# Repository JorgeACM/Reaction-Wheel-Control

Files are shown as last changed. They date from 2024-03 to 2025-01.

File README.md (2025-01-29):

# 🚀 Reaction Wheel Control of an Air-Bearing Floating Robot  

## 📌 Overview  
This repository contains the code and simulation models for the **attitude control system** of an **air-bearing floating robot** using a **reaction wheel with a single degree of freedom**. This project was developed as part of the **MSc in Space Engineering** at the **University of Surrey - Surrey Space Centre**, aiming to simulate **near-frictionless conditions** similar to those in space.  

## 📂 Repository Structure  
```
Reaction-Wheel-Control/
│── CAD/                     # CAD files of the floating robot assembly
│── CAD_Images/              # Images of the robot model
│── Images/                  # Simulink Simulations ScreenShots
│── src/                     # Simulink models and MATLAB scripts for calculations and system simulations  
│── Documents/               # Project-related documents and reports  
│── README.md                # This file  
```

## ⚙️ Setup & Usage  

### 1️⃣ Initialize System Variables  
Before running any **Simulink model**, execute the following MATLAB script to load all system variables into the workspace:  
```matlab
run('src/SystemVariables.m');
```
### 2️⃣ Running Simulink Models  
To simulate the **attitude dynamics and control using a reaction wheel**, follow these steps:  

1. Open **MATLAB**.  
2. Navigate to the `src/` directory.  
3. Open the required Simulink model: `src/CompleteControl_SimpleDC.slx`
4. Click **Run** to start the simulation.  

### 3️⃣ Viewing the Full CAD Assembly  
To visualize the **complete robot assembly**, follow these steps:  

1. Open **SolidWorks**.  
2. Navigate to the `CAD/` directory.  
3. Open the following file:  
`CAD/Floating Robot 2.SLDASM`
4. The full 3D model of the robot should load in SolidWorks.

## 🛠 System Components  
- **Reaction Wheel**: Provides the necessary torque for attitude control.  
- **BLDC Motor**: Controls the reaction wheel’s angular velocity.  
- **Air-Bearing System**: Reduces friction, simulating space-like conditions.  
- **MATLAB/Simulink**: Used for system modeling, simulation, and control design.  

## 📌 Research Contributions  
This project contributes to the **development of reaction wheel-based attitude control systems**, which are widely used in **CubeSats** and other small spacecraft. The system has been validated through numerical simulations and CAD modeling, providing a foundation for further experimental testing.  

## 📖 References  
For a detailed explanation of the system design, refer to the **thesis document** included in the `Documents/` folder:
`Documents/Reaction_Wheel_Control_of_an_Air-Bearing_Floating_Robot.pdf`

## 📝 License  
© 2024 Jorge Antonio Chavarín Montoya.  
This project is part of academic research and is distributed for educational and research purposes.

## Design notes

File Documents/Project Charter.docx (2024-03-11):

GENERAL PROJECT INFORMATION
Project Name | Project ID / Number
Reaction Wheel Control of Air-Bearing Floating Robots
| Date Prepared
| 08-March-2023

Project Sponsor

University of Surrey
Project Manager | Customer
Jorge Chavarin | -

Other Project Stakeholders

Surrey Space Centre

Dr. Nicola Baresi

Stakeholders Responsibilities

Jorge Chavarin – Master student build the project,

Dr. Nicola Baresi – Project Tutor,

University of Surrey / Surrey Space Centre – Lend facilities and tools to do the project.

SCOPE STATEMENT

Business Need and Problem Statement

The Air-Bearing floating robot of the Surrey Space Centre, needs an Attitude Control System to be able to orientate to a specific point (angle) detected by a camera in the “sky”.

Project Goals and Objectives (Deliverables)

- Design a 3D model of the robot, within any assemble errors, and find its moment of inertia, using SolidWorks, within the first 2 weeks.
  - FEPS Faculty Admin, Luca Ferrian, to provide partial design of the robot, missing parts should be created in 3D with same measurements as the real ones from the floating robot.
  - 1-2 weeks
- Design and model the Reaction Wheel system in SolidWorks, according to robot measures. The system includes the motor, wheel, bearings, shaft, sensors (gyroscopes), frame and adaptors, electronics (Raspberry Pi, camera) and any other part used for the Attitude Control system. (1-2 weeks)
- Design a control law for the system in Simulink in order to have a correct reaction of the simulated plant (Software in the Loop).
- Robot will rotate precisely to the given angle in a time frame.

Benefits

Metrics

- Angle precision.
- Time of rotation / angular velocity of the robot.

SUPPORTING DETAIL

Cost

- MATLAB with Simulink license (TBD)
- SolidWorks license (TBD)
- Manufacturing /3D print of pieces (TBD)
- Hardware (£105 - £150)
  - Raspberry Pi (£64-£78)
  - Raspberry case with Fan (£10)
  - Camera (£26-£57)
  - Camera Mount (£5)
  - BDCL motor 536-6024 (£54.84)

Project Completion Date

- First Report: 13/03/2023
- Interim Review: 29/04/2023
- Final Report: 03/09/2023
- Viva Presentation: 03/09/2024 – 15/09/2023

Assumptions

Links to Strategic Objectives and/or Other Projects

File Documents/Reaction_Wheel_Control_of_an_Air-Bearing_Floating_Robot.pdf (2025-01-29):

Jorge Antonio Chavarín Montoya, MSc dissertation

- i -

# Reaction Wheel Control of an Air-Bearing Floating

# Robot

## Jorge Antonio Chavarín Montoya

## Master of Science in Space Engineering

## from the

## University of Surrey

## School of Computer Science and Electronic Engineering

## Faculty of Engineering and Physical Sciences

## University of Surrey

## Guildford, Surrey, GU2 7XH, UK

## September 2024

## Supervised by: Nicola Baresi

## ©Jorge Antonio Chavarín Montoya 2024

- ii -

## DECLARATION OF ORIGINALITY

I confirm that the project dissertation I am submitting is entirely my own work and that any ma-

terial used from other sources has been clearly identified and properly acknowledged and referenced.

In submitting this final version of my report to the JISC anti-plagiarism software resource, I confirm

that my work does not contravene the university regulations on plagiarism as described in the Student

Handbook. In so doing I also acknowledge that I may be held to account for any particular instances

of uncited work detected by the JISC anti-plagiarism software, or as may be found by the project

examiner or project organiser. I also understand that if an allegation of plagiarism is upheld via an

Academic Misconduct Hearing, then I may forfeit any credit for this module, or a more severe pen-

alty may be agreed.

Reaction Wheel Control Of An Air-Bearing Floating Robot

Jorge Antonio Chavarín Montoya

Author Signature | Date: 10/09/2024

Supervisor’s name: Dr. Nicola Baresi

- iii -

## WORD COUNT

Number of Pages: 65

Number of Words: 13406

- iv -

## ABSTRACT

The main objective of this project is to design and implement an Attitude Control System (ACS)

utilizing a single-degree-of-freedom Reaction Wheel for an air-bearing floating robot owned by the

Surrey Space Centre. This system controls the robot’s simulating near-frictionless conditions like to

those in space. The ACS uses mathematical models, control laws, and software-in-the-loop (SIL)

testing to guarantee that the system meets operational standards.

The reaction wheel system, powered by a brushless DC (BLDC) motor, generates the torque re-

quired to adjust the robot’s attitude. The BLDC motor allows precise control over the wheel’s speed,

which directly influences the accurate control of the robot’s orientation. The CAD design and mate-

rial selection were important steps for the smooth integration of all components, helping the system

function as a whole.

The control law achieved in this project lets the system perform attitude adjustments and orienta-

tion changes with accuracy. Initial tests of the reaction wheel showed positive results, giving a solid

base for implementing a functional prototype of the ACS as the next step.

This research contributes to the growing knowledge of attitude control systems for small satellites,

such as CubeSats. The results are a control system that can be tested in real-time simulations, and a

CAD model of the robot useful for future components integrations. This work has potential use in

academic and industrial settings, especially in satellite development.

- v -

## TABLE OF CONTENTS

Declaration of originality | ii
Word Count | iii
Abstract | iv
Table of Contents | v
List of Figures | vii
1 Introduction | 2
1.1 Background and Context | 2
1.2 Scope and Objectives | 3
1.3 Achievements | 3
1.4 Overview of Dissertation | 4
2 Background Theory and Literature Review | 5
2.1 Air-bearing Floating Robots | 5
2.2 Attitude Dynamics | 6
2.3 Reaction Wheels | 8
2.4 Linear Control Theory | 10
2.4.1 Controllability | 10
2.4.2 Observability | 10
2.4.3 Full-state feedback controller | 10
2.5 MATLAB / Simulink | 11
2.6 Summary | 12
3 Robot Model | 13
3.1 Introduction | 13
3.2 Air-Bearing Floating Robot | 13
3.2.1 CAD Design | 13
3.2.2 Inertia measurements | 15
3.3 Reaction Wheel Design | 16
3.3.1 BLDC Motors vs DC Motors | 16
3.3.2 Wheel measurement & material selection | 18
3.3.3 CAD Design | 19
3.3.4 Inertia | 21
3.4 Summary | 22
4 Robot Attitude dynamics and Control via Reaction Wheel | 23
4.1 Introduction | 23
4.2 Coordinate Frames | 23
4.2.1 Inertial Frame vs Rotational Frame | 23

- vi -
4.2.2 Table Frame | 24
4.2.3 Body Frame | 24
4.2.4 Orbit Frame | 24
4.3 Robot Kinematics Equations – Passive Control of Reaction Wheel | 24
4.3.1 Controllability of Outer Loop | 25
4.3.2 Observability of Outer Loop | 26
4.4 Control Torque with Reaction Wheels in Passive Mode | 26
4.5 Reaction Wheel dynamics | 26
4.5.1 Motor Electrical & Mechanical Equations | 26
4.5.2 Three-Constant motor model DC representation | 27
4.6 Summary of Mathematical Developments | 30
5 Numerical Simulations in Simulink | 30
5.1 Introduction | 30
5.2 Simulink Models | 31
5.2.1 Outer Loop | 31
5.2.2 Inner Loop | 34
5.3 Numerical Experiments | 37
5.4 Summary | 40
6 Conclusion | 41
6.1 Evaluation | 42
6.2 Future Work | 43
6.2.1 PWM Implementation for BLDC Motors | 43
6.2.2 No Body and Axis of Inertia Alignment | 43
7 References | 44
8 Appendix | 46
8.1 APPENDIX A: Coordinate System Definition (CSD) Document | 46
1. Overview of Coordinate Systems | 46
1.1 Summary | 46
1.2 Frank Diagram | 46
2. Coordinate Systems | 47
2.1 | Attitude Reference Frames | 47
2.2 | Mechanical Frames | 49
APPENDIX B: MATLAB Scripts & Simulink Models | 58

- vii -

## LIST OF FIGURES

Figure 2-1 – ESA Air-Bearing Floating Robot. Credit: ESA-G/Porter – CC BY-SA 3.0 IGO [4]..... 5

Figure 2-2 - Full-State Feedback Controller Block Diagram | 11
Figure 3-1 - Air-bearing Floating Robot from Surrey Space Centre | 13
Figure 3-2 - CAD Design with subsystems in distinct levels | 14
Figure 3-3 - Top-view of Robot showing counterweights circled in yellow | 15

Figure 3-4 - Traditional DC brushed motor with a permanent magnet stator. Credit: ZGC Motor [13].

| 16
Figure 3-5 - Brushed Motor vs Brushless DC (BLDC) Motor [14] | 17
Figure 3-6 - GM3506 BLDC Motor with AS5048A Encoder integrated [17] | 17
Figure 3-7 – 2-D Drawing of Reaction Wheel. Measurements in mm | 19
Figure 3-8 - Wheel CAD | 19
Figure 3-9 - Reaction Wheel System Assembly | 20
Figure 3-10 - Motor Base with measurements | 20
Figure 4-1 – Three-constant motor model DC representation of a three-phase motor | 27
Figure 4-2 - Momentum exchange devise model | 28
Figure 4-3 - Reaction Wheel in torque mode | 29
Figure 5-1 - Outer Loop - Robot Attitude Control | 31
Figure 5-2 - Open-Loop Step Response of Attitude Control | 32
Figure 5-3 - Step Response for different Poles | 33
Figure 5-4 – Poles location using Full-State Feedback Control, P1(-4.89,0), P2(-3.998,0) | 33
Figure 5-5 - Closed Loop Step Response of State Feedback Controller | 34
Figure 5-6 -Simplified Torque Mode of a Reaction Wheel | 34

Figure 5-7 - Step Response of Simplified Torque Mode Reaction Wheel without limited Torque. 36

Figure 5-8 - Pole location of Reaction Wheel System | 36
Figure 5-9 - Complete Robot Attitude Controller | 37
Figure 5-10 – Step response of amplitude 10-degrees. Gains: Kp = 1.0002, Kd = 04547 | 38
Figure 5-11 - Step response for a 170-degrees step. Gains Kp = 1.0002, Kd = 04547 | 38

Figure 5-12 – Top: Comparison between the angular velocity of the robot and the reaction wheel.

Bottom: Commanded torque vs actual torque reaction of the robot | 39
Figure 5-13 – Plant Step response of amplitude 170 (deg.). Gains Kp = 0.9 & Kd = 1 | 40
Figure 6-1 - PWM Sensorless Controller of a BLDC motor | 43
Figure 8-1: Right hand Rule | 46

Figure 8-2. Frank Diagram. “T” stands for translation, “R” for rotation and “A” refers to the Attitude

Dynamics equations | 46
Figure 8-3: GTS reference frame | 47

- viii -
Figure 8-4: RTS Reference Frame | 48
Figure 8-5. Body Fixed Reference Frame & Mechanical CAD Frame Below | 50
Figure 8-6. CAD Reference Frame. The point is at O (0,0,0) of the CAD Frame | 52
Figure 8-7. Reaction Wheel Frame vs Mechanical CAD Frame | 53
Figure 8-8. Camera Reference Frame (CAM), Mechanical Frame (CAD) | 56
Figure 8-9. Distance from Mechanical Frame to Gyro Frame | 57
Figure 8-10. Gyroscope Frame and Mechanical CAD Frame | 57

- 2 -

## 1 INTRODUCTION

Attitude control systems (ACS) are important for spacecraft and robotic platforms that need to func-

tion in frictionless environments. These systems help a satellite or robot reach and maintain the

desired orientation, which is crucial for mission success. In this project, an ACS was designed and

implemented for a floating robot that uses a reaction wheel as its main actuator.

The system's goal is to control the robot's orientation with high precision in real-time. This is

accomplished by combining hardware components such as sensors and actuators with control algo-

rithms tested through software-in-the-loop simulations, being the latter the main objective of this

project. The floating platform, built to simulate microgravity conditions, provides a way to test the

ACS’s performance in real conditions.

### 1.1 Background and Context

In recent years, reaction wheel systems have become one of the most used attitude control systems

for small satellites due to their accuracy capacity and no fuel necessity. Meanwhile, the need to test

these and other spacecraft subsystems on the ground caused scientists to develop different ways to

simulate space environments. Air-bearing spacecraft simulators have been used to test attitude deter-

mination and control systems for more than 45 years [1]. These robots use air-bearing technologies

to float over surfaces, therefore simulating minimal torque environments.

Reaction Wheels are used to precisely orientate a small spacecraft in a desired direction, so they

are tested in air-bearing floating robots. By using the principle of conservation of angular momentum,

reaction wheels provide the required torque to adjust the robot's orientation in response to external

disturbances or desired manoeuvres. The system comprises one or more motor-driven wheels

mounted on the satellite's body that accumulate rotational energy. Any change in the angular accel-

eration of the wheel causes an equal and opposite reaction, thereby enabling the robot to achieve a

specific angular momentum.

Space applications avoid mechanical contact, such as bearings, gears, or motor brushes. Conse-

quently, brushless DC motors (BLDC) are becoming more relevant, as they have longer lifespan,

higher torque and efficiency, and low heat dissipation than traditional DC motors [2].

The objective of this project is to design, manufacture, and test a single-degree-of-freedom reac-

tion wheel system for a floating robot. With the aid of existing literature and practical observations,

this research seeks to explain the fundamental principles, design considerations, and implementation

challenges associated with the integration of a reaction wheel control system into ait-bearing floating

robots.

- 3 -

### 1.2 Scope (http://www.cs.stir.ac.uk/~kjt/research/conformed.html) and Objectives

1. CAD design of air-bearing device equipped with a Reaction Wheel assembly, the model shall

include a power source, a raspberry pi, and IMU unit, and a camera module to estimate the

attitude of the “spacecraft”, the reaction wheel and motor shall be sized and included in the

model to enable attitude control experiments.

2. Develop a PID controller in MATLAB Simulink for the 1-DOF attitude control of an air-

bearing robot on granite table by means of a reaction wheel.

3. The robotshall re-orient itself based on commanded “desired” attitude configurations, in Sim-

ulink simulations.

To achieve the first objective, a detailed CAD model of the air-bearing floating robot equipped

with a reaction wheel assembly was created using SolidWorks. The design included a power source

(LiPo Battery), a Raspberry Pi, a Gyroscope, and a camera module for estimate the robot’s attitude.

The reaction wheel and motor were sized and integrated into the model according to the robots wight

and inertia measurements.

For the second objective, a controller was developed in MATLAB and Simulink to handle the 1-

DOF attitude control of the robot using the reaction wheel. Main controller gains were deduced math-

ematically, and subsequent real-time simulations were performed to adjust the controller.

Finally, simulations were run to check that the robot could reorient itself based on user-com-

manded “desired” attitude configurations. The Simulink tests showed that the robot adjusted its

orientation smooth and correctly, according to the input commands. While physical tests have yet to

be completed, the simulations suggest that the system meets the expectations for this task..

### 1.3 Achievements

The main accomplishment of this project is the successful development of an Attitude Control Sys-

tem (ACS), which includes both mechanical design of its components and the CAD design of the

floating robot SolidWorks. The 3D model created ensures the compatibility among its components

and gives a framework for integrating future projects, making it easier to adapt or extend the system

as needed. This model supports future work by offering a solid base for additional modifications.

Additionally, the mathematical model for the robot and the Acs, was used to simulate the dynam-

ics of both plants. This model makes possible to predict the system’s behaviour, forming the basis

for the control law proposed in this project. It also offers valuable insight for potential improvements

or alternative control strategies that could be explored in future research.

The project also achieved successful software-in-the-Loop (SIL) testing using Simulink and

MATLAB. This testing confirmed that the developed control law functions effectively and helped in

- 4 -

fine-tuning it by running real-time simulations of the system’s performance. Overall, these achieve-

ments lay a strong foundation for future development in attitude control systems for small platforms.

### 1.4 Overview of Dissertation

This dissertation is structured into several chapters and subchapters that describe the complete pro-

cess from background review and conceptualization to implementation and testing of the system.

The first chapter provides the background and objectives of the project. It introduces the concept

of Attitude Control Systems and explains why reaction wheels are a preferred solution for small

platforms like CubeSats.

Chapter 2 gives an overview of the theoretical concepts and research that form the basis of the

Attitude Control System. It also introduces the concept of floating robots as testing mechanisms for

spacecrafts systems. Additionally, it covers attitude dynamics, reaction wheel operation and control

laws used later in the project. The chapter reviews relevant literature on the use of reaction wheels

in small satellites, which influenced the design choices made for the project.

The third chapter explains the physical and mathematical modelling of the floating robot. It in-

cludes a description of the robot’s structural components, with CAD designs created in SolidWorks.

This chapter also explains the decisions regarding material selection and measurements. It compares

conventional DC motors with Brushless DC (BLDC) motors and discusses the advantages and chal-

lenges of using BLDC motors in space applications.

Subsequently, Chapter 4 dives into the attitude dynamics of the robot and the control strategies

used to adjust its orientation. It describes the coordinate frames necessary to describe the robot’s and

components movements. Also, it focuses on the interaction between the reaction wheel and the robot,

detailing how the wheel generates the torque required to rotate the robot. The mathematical models

presented in this chapter serve as the basis for understanding the control laws developed later in the

chapter.

Chapter 5 covers the simulation work performed to test the ACS, using Simulink. The control

algorithms and models developed in the previous chapter are tested and evaluated in this section.

This chapter also details the refinement of control strategies done through real-time testing.

Finally chapter 6 gives some conclusions about the complete report, evaluates if the main objec-

tives were accomplished and give options for future work regarding reaction wheels.

- 5 -

## 2 BACKGROUND THEORY AND LITERATURE REVIEW

### 2.1 Air-bearing Floating Robots

Air-bearing floating robots have been used since the middle of last century to simulate microgravity

conditions and spacecraft dynamics on Earth, becoming essential for developing and testing real

space applications under controlled environments, such as attitude control systems or spacecraft ma-

noeuvres.

This type of robot possesses air-bearings that create a thin layer of pressurized air between the

spherical or planar surface of the robot and the surface on which it hovers, as shown in Figure 2-1.

The pressurized air is expelled through small holes on the base of the robot, forming an air layer that

drastically reduces the friction between the robot and the surface [3]. As a result, the robot can move

freely in any direction with lower resistance, simulating the space microgravity environment.

The air system allows the robots to simulate an almost frictionless environment. By adjusting the

pressure and direction of the air expelled, the movements of the robots can be controlled with preci-

sion, which allows them to replicate real dynamics conditions that objects would experiment with in

space, such as the absence of gravity and atmospheric drag.

Figure 2-1 – ESA Air-Bearing Floating Robot. Credit: ESA-G/Porter – CC BY-SA 3.0 IGO [4].

Air-bearing platforms have evolved significantly over time. While early systems were initially

designed for academic purposes, they quickly became indispensable for testing real spacecraft appli-

cations. Floating robots allows the simulation of rotational dynamics in an almost frictionless

environment [1].

- 6 -

In recent years, the capabilities of air-bearing floating robots have improved thanks to technolog-

ical advancements, enabling them to emulate more complex manoeuvres, such as multiple axes

satellite rotations, without the friction restriction of Earth surfaces. Additionally, the continuous evo-

lution of air-bearing floating robots reflects the growing interest in space exploration and their

importance as space missions get more ambitious and challenging.

Floating robots have helped to develop new control law techniques, such as the ones used on

reaction wheels, implemented mainly in CubeSats to maintain their stability and orientation. How-

ever, one of the main constraints is the scale of these spacecraft’s simulators, typically limited to

small or medium-size platforms, where emulating the dynamics of bigger spacecrafts still represents

a challenge.

### 2.2 Attitude Dynamics

Attitude Dynamics refers to the study and control of orientation of a rigid body, relative to an inertial

frame of reference or another object (such as the Earth or the Sun). This field is important for the

stability and control of spacecrafts in space, as it determines how a spacecraft or satellite orientates

its principal axes with respect to such reference frame. In order to realize specific tasks like antenna

or camera pointing, or orbital manoeuvres, spacecrafts must be able to control their attitude.

The attitude of a satellite or spacecraft cand be defined through three main angles: roll, pitch and

yaw, called Eule angles(ϕ, θ, ψ). Those angles describe the rotation of the spacecraft over its principal

axes. Alternatively, rotation matrices or by an axis-angle vector (Euler axis and principal angle), that

also describe the attitude of the spacecraft. Additionally, quaternions have some advantages in terms

of describing rotations in a three-dimensional space avoiding singularities that Direction Cosine Ma-

trices (DCM) have. The selection of the appropriate representation of the attitude is related to the

requirements of the mission. While quaternions avoid mathematical singularities, Euler angles rep-

resentation is the simplest method to describe a spacecraft attitude.

Furthermore, the equations of movement for attitude dynamics of a satellite can be described of

how its orientation changes over time under the influence of external or internal torques. By control-

ling those torquesthe satellite could maintain or rotate to desired orientation. The equations of motion

for the attitude dynamics derive from the Euler equations, that describe the rotational behaviour of a

rigid body. Equation (2.1) relate the external torques acting in the spacecraft with the rate of change

of its angular momentum:

τ = ḣ

I = ḣ
B − ω × h | (2.1)

Where:

- h is the angular momentum vector,

- 7 -
- τ is the torque vector and,
- ω is the angular velocity vector.

The subscript ‘I’ on the equation above indicates a derivative in the inertial reference frame, and

the subscript ‘B’ indicates derivative in the body frame.

Moreover, the angular momentum is a vector quantity that reflects the rotational motion of a body.

Mathematically it can be defined as:

h = Iω̇ | (2.2)

Where the inertia tensor of the body, I, is matrix that represents how the mass of the satellite is

distributed in relation to their axis of rotation. If the coordinate system of the body is aligned to its

main axis, called principal axis of inertia, the matrix is diagonal, simplifying calculations associated

with the rotation of the body:
[
Ixx | 0 | 0
0 | Iyy | 0
0 | 0 | Izz] | (2.3)

Where Ixx, Iyy, and Izz are the principal moments of inertia around the x, y, and z axes, respectively.

However, it the tensor of inertia is represented in a different coordinate system (i.e. when the mas

of the body is not symmetrically distributed with respect to the principal axes), it is represented as:
[
Ixx | Ixy | Ixz
Iyx | Iyy | Iyz
Izx | Izy | Izz] | (2.4)

The products of inertia, Ixy= Iyx, Ixz= Izx, and Iyz= Izy, indicate how the rotation around one of the

axes is coupled with the rotation around another of axis.[5]

If we define the angular velocity vector as:

ω = [ωx | ωy | ωz] T
, | (2.5)

and assuming XB, YB, ZB are the principal axes of inertia, by substituting equation (2.2) in equation

(2.1) and performing the cross product, the scalar quantity of the torque for each axis can be defined

as:

τx = Ixω̇x + ωyωz(Iz − Iy) τy = Iyω̇y + ωxωz(Ix − Iz) τz = Izω̇z + ωxωy(Iy − Ix)

(2.6)

In this project, the attitude control of the floating robot is done through a reaction wheel system,

as the objective is to reorientate the robot into a desired direction.

- 8 -

### 2.3 Reaction Wheels

The principle of conservation of angular momentum establishes that in the absence of external tor-

ques, the angular momentum of a system remains constant. Reaction and momentum wheels take

advantage of this principle to control and stabilize the orientation of the spacecraft. Both systems

spin to generate a reaction torque that can change the orientation of the satellite without applying any

external forces.

The main difference between them lies in their mode of operation. On one hand, reaction wheels

are designed to adjust their rotational velocity to change the satellite’s orientation. They are used to

make precise manoeuvres by increasing or decreasing their angular velocity to generate an angular

momentum that reorientates the spacecraft in the desired direction.

On the other hand, momentum wheels spin at a high and constant velocity, providing stability to

the satellite. Their main function is to stabilize the attitude of the satellite against external disturb-

ances, keeping it in a fixed orientation. While reaction wheels focus on the adjustment and active

control of the attitude, momentum wheels centre on passive stabilization, resisting unwanted changes

in orientation [6].

Reaction Wheels are a key component in spacecraft attitude control, as they can adjust and main-

tain spacecraft orientation very precisely [7]. Their simplicity and effectiveness have made them

adopted in many space missions, from Earth observation satellites to deep space exploration.

The precise control of the spacecraft attitude by reaction wheels, without any external forces,

allows the satellite to realize sustained operations in space, where other traditional methods involving

thrusters would be limited by fuel consumption. Their capacity to generate a reaction torque inter-

nally improves the spacecraft’s lifetime. Also, it contributes to the stability and manoeuvrability

needed in complex operations, such as remote sensing operations and satellite alignment for com-

munications.

Initial designs were big and limited in their operational range, which required high amount of

power and were less flexible when performing manoeuvres. However, technology advances have led

to the development of more compact, efficient, and durable systems. Modern reaction wheels operate

at higher velocities, offering better control over the spacecraft’s angular momentum and enabling

more agile manoeuvres than before.

Integration of reaction wheel subsystems into spacecraft implies several considerations and engi-

neering challenges. One of the principal problems is wheel saturation. This occurs when the reaction

wheel reaches its maximum angular velocity and, therefore, cannot provide any extra torque. In order

to mitigate this issue, reaction wheel subsystems are commonly complemented with magnetorquers

or thrusters that work together with reaction wheels to desaturase them, restoring the capacity of the

- 9 -

wheel to provide torque. This combination ensures the continued capacity of attitude control [10].

Additionally, the configuration of the reaction wheels in the spacecraft depends on the specific

requirements for each mission, where redundancy or failure tolerance must be considered. The three

most common mount configurations of reaction wheels are Three-Orthogonal Wheel Configuration,

Four-Wheel Tetrahedral (or Pyramidal) Configuration, and Three-Wheel Skewed Configuration. The

first configuration is the simplest and widely used in missions where simplicity and power efficiency

are paramount. In this configuration, the three wheels are aligned to the principal axis of the satellite

(XB, YB, ZB), which allows them to control the attitude on the three axes with the minimum compo-

nents possible. However, this design has no redundancy, meaning the control over one of the axes

will be lost if a wheel fails.

Instead, the wheels are mounted at a non-orthogonal angle in the Four-Wheel Pyramidal Config-

uration, providing the satellite with complete redundancy. If one of the wheels fails, the remaining

three wheels can still control the spacecraft’s attitude. This configuration is the most used when reli-

ability is of high importance.

Finally, the Three-Wheel Skewed Configuration, although it is more complex than the orthogonal

configuration, offers an equilibrium between simplicity and limited redundancy. In this case, the

wheels are mounted at specific angles, which allows a certain control level even with one-wheel

failure without adding an extra wheel. This configuration is most suitable for missions with space

and budget restrictions but requires some redundancy.

With the rise of small satellites, such as CubeSats, the need for smaller and lighter reaction wheels

adjusted to space and power restrictions has emerged. Modern reaction micro-wheels maintain high

performance despite their compact size, letting these new small satellites reach the same attitude

control level as their bigger counterparts.

Furthermore, the design of satellites using Commercial Off-the-Shelf (COTS) components has

gained popularity over the last few years, including reaction wheel systems. The use of COTS lets

the owners reduce development costs and time by taking advantage of standard mechanics and elec-

tronic components that are easily available in the market. For the specific case of reaction wheels,

BLDC and DC motors of high precision and electronic controllers are the most common and acces-

sible options of COTS for reaction wheels. In this way, integration with external subsystems can be

easily achieved using standards already used and tested in other industries. Even though the use of

COTS implies certain limitations in durability or personalization of components, the technological

advancements and high-quality components available in the market have made these options more

viable for more space missions.

- 10 -

### 2.4 Linear Control Theory

Linear Control Theory is used to analyse dynamic systems described through linear differential equa-

tions. This theory is applied in control engineering to design systems that maintain stable behaviour

and respond adequately to external perturbations. Representing these systems through equations in

the state space gives a complete vision of their dynamics, considering inputs and outputs.

### 2.4.1 Controllability

A system is fully controllable if every state vector can be transferred from any initial state to any

other state in a finite time through an adequate control signal. Mathematically, a continuous system

described by:

ẋ = Ax + Bu | (2.7)
y(t) = Cx + Bu, | (2.8)

is fully controllable if the controllability matrix QC (see eq. 2.8) has a complete range. In other words,

if the range is equal to the number of stated n, where the matrix A is a n × n square matrix.

QC = [B AB A
2B … A
n−1B] | (2.9)

When the condition of full controllability is met, the system can be manipulated to reach any

desired state [11].

### 2.4.2 Observability

The observability of a system refers to the capacity to deduct the complete state of the system from

observing its outputs in a finite time. A system is fully observable if it is possible to determine the

system's initial state with the information of the output y(t) through time. Mathematically, a system

described by equations (2.7) and (2.8) is fully observable if its observability matrix from equation

(2.10) has a complete range.

QO = [C

T A

TC

T … (A

T
)

n−1C

T]

T
(2.10)

Observability is especially important in systems where not all the states can be measured directly,

and it is necessary to reconstruct the non-observable states from the available outputs.[11]

### 2.4.3 Full-state feedback controller

Through the full-state feedback controller, the system dynamics, like stability and response time, can

be adjusted by using all the state variables, see Figure 2-2. This method is based on the relation:

u = −Kx, | (2.11)

where K is the gain matrix of the controller. With a correct designed of this matrix, it is possible to

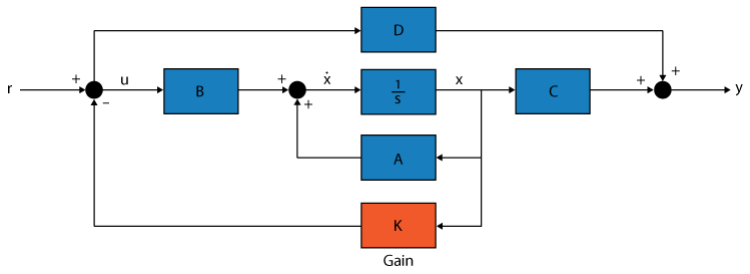
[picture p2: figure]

- 11 -

locate the poles of the system in closed loop in desired locations of the complex plane, as long as the

original system is fully controllable. This strategy is convenient when the dynamic behaviour of the

system must be adapted to design specifications.[11].

To compute the matrix K, the eigenvalues of the closed-loop system must be replaced at desired

positions to achieve the required performance. Given the state-space system from (2.7) and the con-

trol law (2.11), the closed-loop dynamics are expressed in (2.12), where r is the reference input [12].

The matrix K is selected toshift the eigenvalues of A − BK to the desired locations.

ẋ = (A − BK)x + Br | (2.12)

This type of controller requires observability from all the states, which is not always feasible in

practice. To address this, an observer is added to the system. This observer is responsible for estimat-

ing the non-measurable states from the system's outputs, thereby enhancing the controller's

effectiveness.

Figure 2-2 - Full-State Feedback Controller Block Diagram

### 2.5 MATLAB / Simulink

MATLAB is a high-level programming environment used for numerical computing, data analysis,

and algorithm development. It provides various tools for tasks such as matrix operations, plotting

functions and implementing algorithms, making it very useful for engineering and scientific appli-

cations. In this project, MATLAB was used to develop and simulate the state-space representation of

both systems, to plot almost all graphs presented in this document, and to validate the controllability

and observability of the system, among other functions that are annexed in APPENDIX B: MATLAB

Scripts & Simulink Models.

Simulink is an extension of MATLAB that provides a graphical interface for modelling, simulat-

ing and analysing dynamic systems. In this project, Simulink was used to simulate the robot’s attitude

control system, including the reaction wheel, and the controller, in block diagram. Through Simulink,

real-time simulations were performed to fine-tune the control algorithm and review the systems per-

formance.

- 12 -

### 2.6 Summary

This chapter discussed the history and significance of air-bearing floating robots in simulating mi-

crogravity and space dynamics for satellite and spacecraft applications. Attitude dynamics was

explored to describe how angular momentum can be used to rotate and change orientation of rigid

bodies. Moreover, the functionality of reaction wheel systems, in terms of how they can control and

stabilize satellites orientation by leveraging the principle of conservation of angular momentum and

the benefits of the different mount configuration of reaction wheels were also boarded. Additionally,

this chapter covered fundamental control concepts, such as controllability and observability and the

Full-State Feedback Controller, that will be used in future chapters where the complete control of the

system is going to be described.

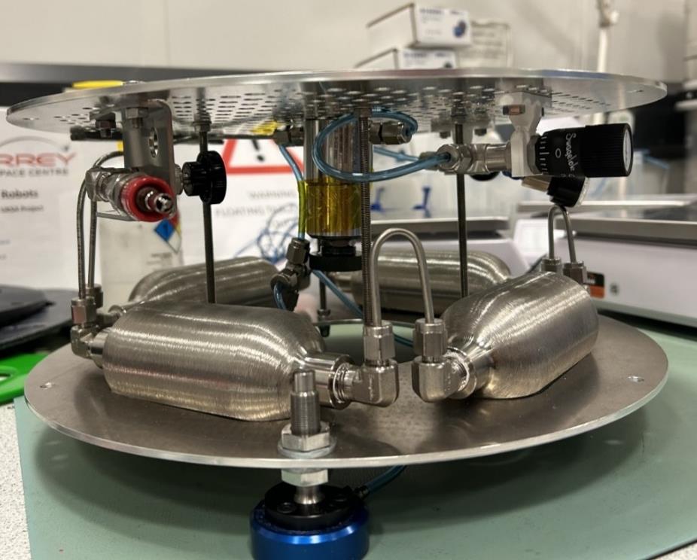
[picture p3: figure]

- 13 -

## 3 ROBOT MODEL

### 3.1 Introduction

This chapter focuses on the design and implementation of the reaction wheel system as part of the

air-bearing floating robot. A modular structure of various subsystems including a 2S-LiPo battery, a

Raspberry Pi, and an inertial measurement unit (IMU), are integrated to the main structure of the

floating robot from Surrey Space Centre. The reaction wheel, part of the Attitude Control system,

was designed using SolidWorks, ensuring it meets the required moment of inertia for accurate con-

trol. This chapter delves into the CAD design, material selection and the integration of the reaction

wheel with the motor, providing an overview of the processes involved in the design and manufacture

of an Attitude Control system.

### 3.2 Air-Bearing Floating Robot

### 3.2.1 CAD Design

The robot was modelled using SolidWorks with the objective to get the necessary measurements for

the design and integration of additional subsystems, such as the reaction wheel, and different sensors.

The robot, property of Surrey Space Centre, had three air tanks, a pressure pump, three air-bearings,

valves, and air hoses (see Figure 3-1). While most of the components’ measurements were obtained

directly from the manufacturer, some were unavailable, requiring physical measurements to be taken

manually. The upper and lower disks were made of 1060 Aluminium Alloy, while the air tanks and

valves were made of 316L Stainless-Steel to withstand high internal pressures.

Figure 3-1 - Air-bearing Floating Robot from Surrey Space Centre

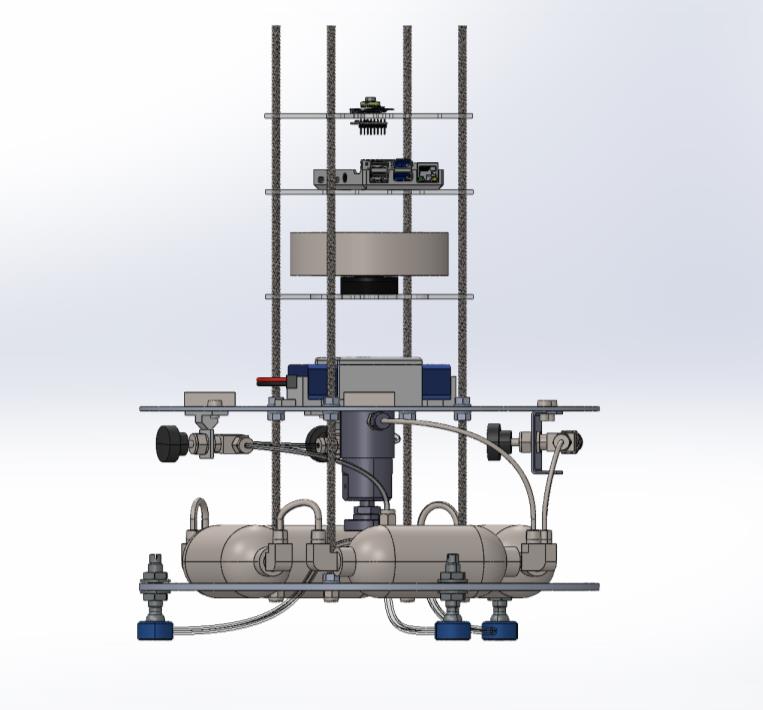
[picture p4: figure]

- 14 -

Once the main structure was modelled, electronics components were added, including a 2S-LiPo

battery, a Raspberry Pi, a Pi-Cam, and the Inertial Measurement Module (IMU) along with their

corresponding mounts. The structure of the robot was designed to be modular, with the power sub-

system, sensors, On-Board Computer, and reaction wheel placed on different levels, following the

CubeSat Standard (as shown in Figure 3-2).

The CAD model of the robot is fundamental for simulating of the entire system One of the chal-

lenges encountered was that the spacing between the holes on the top disk was not symmetrical and

the valves were also mounted asymmetrically, causing misalignments in the centre of mass and the

principal axes of inertia. A key strategy during assembly was to align the vertical axis of inertia and

the centre of mass to the geometrical centre of the robot by carefully planning the distribution of

components across the horizontal plane. The reaction wheel was positioned so that its axis of rotation

was as closely aligned as possible with the principal axis of the robot.

Figure 3-2 - CAD Design with subsystems in distinct levels.

Finally, to align the centre of mass and the vertical principal axis of inertia to the vertical axis of

the geometrical body, a pair of counterweights were added. Each counterweight was made of 316L-

SS with a mass of 100.02 g and was placed in specific locations along the horizontal plane of the

robot. Figure 3-3 shows the counterweights location on the top disk. The formula to calculate the

position to place the counterweights in each axis is:

rx =

mrobot ∙ (−∆x)

mcw

(3-1)

Where:

- rx is the location of the counterweight in one axis,

- 15 -
- mrobot is the total mass of the robot,
- ∆x is the misalignment of the centre of mass in the specific axis,
- mcw is the mass of the counterweight.

The precision and correct alignment of the centre of mass are of importance to determine the

proper behaviour of the robot particularly in the relation to the performance of the reaction wheel.

Figure 3-3 - Top-view of Robot showing counterweights circled in yellow.

### 3.2.2 Inertia measurements

From SolidWorks it was possible to obtain metrics of the robot, including weight, the Moments of

Inertia, and the position of the principal axes of inertia with respect a reference frame (explained in

the next chapter). SolidWorks name as X-axis to the minimum axis of inertia, and due to the distri-

bution of weights, that is the vertical axis. Due to the inertial vertical axis was denominated as the Z-

axis a rotation must be made. However, as the objective of the project is to rotate the robot only in

its vertical axis, so just the scalar quantity of the Moment of Inertia in its X-axis is used.

Weight: 6.1299 kg,

Moments of Inertia:

Ix = 0.0511 kg⁄m²

Iy = 0.0809 kg⁄m²

Iz = 0.0839 kg⁄m²

(3-2)

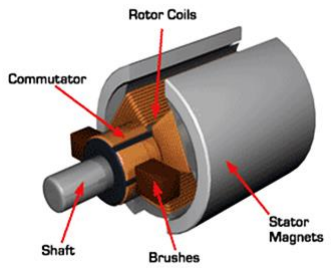
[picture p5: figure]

- 16 -

### 3.3 Reaction Wheel Design

### 3.3.1 BLDC Motors vs DC Motors

DC Motors have been used for over a century, powering from small devices to industrial machines.

However, as the demand for greater efficiency and control has grown, engineers have opted to use

brushless DC motors (BLDC). These motors have outperformed standard DC motors in many appli-

cations, particularly in space, where precision and reliability are of great interest.

Traditional DC motors operate by interacting with a static magnetic field generated by a perma-

nent magnet and a variable magnetic field produced by a coil in the rotor (see Figure 3-4). The rotor

spins when its polarity changes, which is produced by a mechanical commutator with brushes that

maintain contact with the rotating commutator [15]. This simple design allows easy speed and torque

control by adjusting the voltage supplied to the motor.

Nevertheless, the mechanical commutator represents a potential point of failure because the

brushes are subject to wear if there is no periodic maintenance, a problem in space applications where

maintenance is not feasible.

Figure 3-4 - Traditional DC brushed motor with a permanent magnet stator. Credit: ZGC Motor [13].

In contrast, BLDC Motors function with electronic commutation instead of mechanical. The rotor

has a set of permanent magnets, and the coils are fixed on the stator. The commutation of current

through the coils is managed electronically, which provides better control compared to DC motors

and removes the risk of mechanical wear (see Figure 3-5) [15] [16].

Thanks to their robustness and precision, BLDC motors are well-suited for space applications.

However, they require more complex control systemsthat includes sensors to detect the rotor position

and electronic controllers to manage commutation and convert the input voltage into a three-phase

voltage.

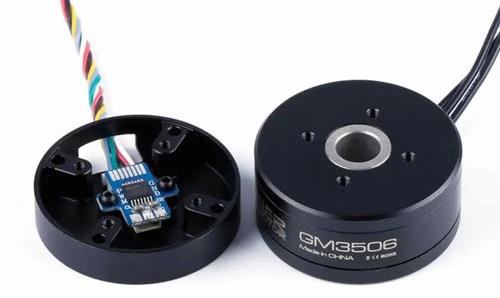
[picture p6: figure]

- 17 -

Figure 3-5 - Brushed Motor vs Brushless DC (BLDC) Motor [14].

Overall, BLDC motors offer a better efficiency -reaching up to 90%- due to the absence of energy

loss brush friction. They are also lighter and more compact than their DC counterparts for the same

power output. Brushless motors allow a more advanced control like velocity modulation or change

of spin direction without additional components but are not as straightforward to control as DC mo-

tors.

The motor used for this project is a GM3506 Brushless. A BLDC was selected as they are more

and more commonly used in space. GM3506 is powerful and reasonably priced, ensuring it can pro-

duce the necessary torque to spin the wheel. Additionally, the motor has incorporated an AS5048A

Encoder, with two types of communication, PWM or I2C, which was another reason to select it.

Table 3-1 shows the specifications of the motor.

Figure 3-6 - GM3506 BLDC Motor with AS5048A Encoder integrated [17].

- 18 -
Spec. | Value
Resistance | 5.6 Ω ± 5%
Weight | 80.3 g
No Load | Voltage | 16 V
| Current | 0.17 ± 0.05 A
| Max. Speed | 2149 – 2375 RPM
Load | Voltage | 12 V
| Current | 1 A
| Torque | 600 – 1000 g*cm

Table 3-1 - Motor GM-3506 Specifications.

The 2S-LiPo battery provides power to the motor, ensuring the motor can provide its maximum

torque indicated in the datasheet.

The maximum torque of the motor, according to Table 3-1, is τ = 600 g ∗ cm = 0.059 Nm. The

acceleration of the robot is calculated from the below equation:

α =

τ

Irobot

(3-3)

Substituting the inertia of the robot in the vertical axis (Ix), calculated at eq.(3-2), the maximum

angular acceleration that the robot can have is α = 1.154 rad
s

⁄ 2.

Lastly, using equation (3-4) the minimum time taken by the robot to execute a complete rotation

(θ = 2π) is t = 3.3 seconds, this can be very fast, however a condition in the control loop can be

added to limit the torque produced by the motor.
t = √
2θ
α

(3-4)

### 3.3.2 Wheel measurement & material selection

The wheel design includes a spoke structure in a 45-degree distribution to reduce its overall weight

while concentrating most of the mass in the outer ring compared to the disk-ring structure. The min-

imization of mass in the centre of the wheel, thanks to the spokes design, contributes to a more

efficient operation of the motor due to the reduction of the load on it. The radius of the outer and

inner circles of the ring are rout = 55 mm and rin = 40 mm, respectively, and a depth of ℎ =

30 mm. The inner disk radius is rdisk = 45 mm, see Figure 2-1. Eight spokes join ring and disk.

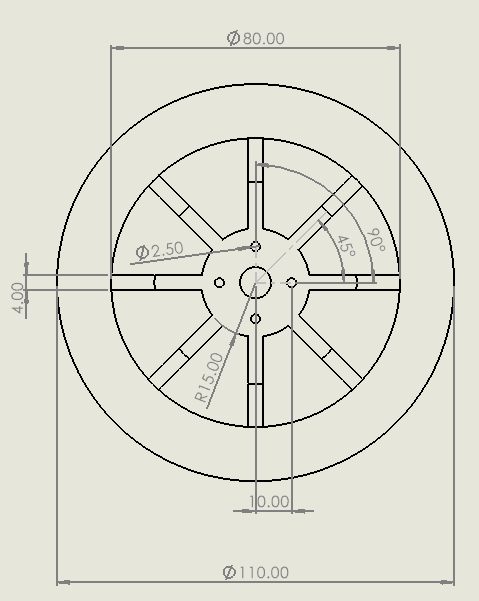
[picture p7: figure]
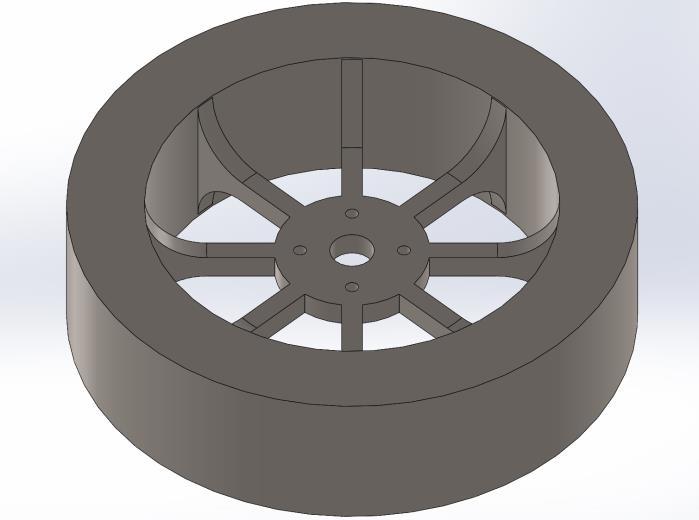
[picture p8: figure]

- 19 -

Figure 3-7 – 2-D Drawing of Reaction Wheel. Measurements in mm.

The reaction wheel was manufactured of 316L stainless steel because of its excellent resistance

to corrosion. Additionally, its high density allows smaller designs with high inertia. However, it is

also a good practice to use an aluminium alloy, depending on the mission.

The wheel design requires to take in consideration the physical and dynamic properties of the system.

### 3.3.3 CAD Design

The wheel design was also carried out using SolidWorks, with the objectives of calculating the

wheel's moment of inertia, manufacturing the wheel, and finally assembling it to the robot. The

wheel, as shown in Figure 3-8, has a central hole in the inner disk to couple it into the motor through

a shaft, and four smaller holes around (diameter = 1.25 mm) for screws to securely attach the wheel

to the motor, preventing any non-desired movement.

Figure 3-8 - Wheel CAD

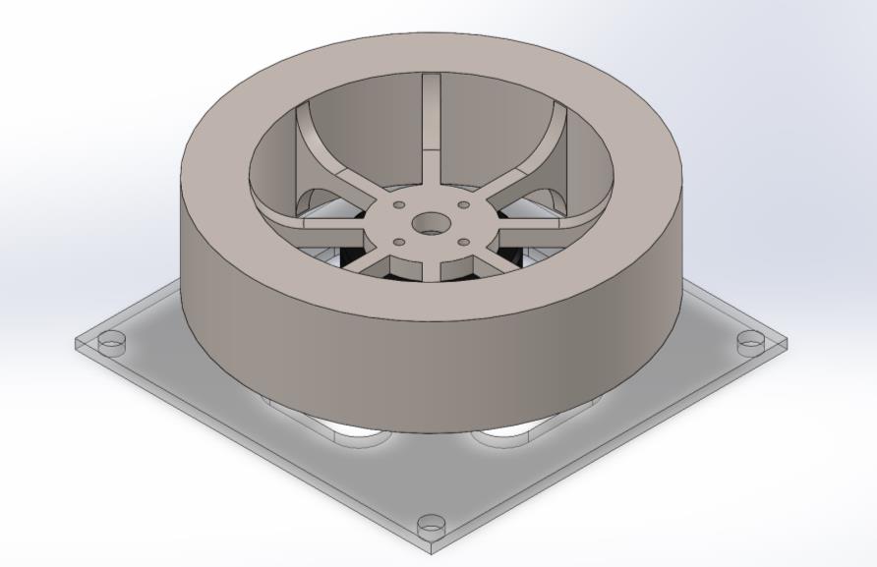
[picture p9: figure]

- 20 -

The width of the spokes and the outer ring of the wheel were adjusted to achieve the desired

moment of inertia. Figure 3-8 shows the wheel, while Figure 3-9 displays the complete reaction

wheel assembly.

Figure 3-9 - Reaction Wheel System Assembly

The base of the motor (Figure 3-10) positions the reaction wheel system at the centre of the robot,

aligning both vertical axes. The base includes four elliptical holes, with a semi-major axis of 17.5

mm and a semi-minor axis of 7.5 mm, to pass the wires from the battery to the motor and to the

raspberry in the upper level.

Figure 3-10 - Motor Base with measurements.

- 21 -

To attach the base to the main screws extending from the robot, an initial hole (diameter = 6 mm)

was designed at a 45-degree angle from the horizontal, with 70 mm from the centre of the base. The

remaining three holes were placed at the corners of a square with sides measuring 98.99 mm.

### 3.3.4 Inertia

The formula that relates the robot’s rotation time for a specific angle with the motor’s speed is given

by:

Irw ∙ ωmotor = 2 ∙ Irobot ∙

θ

trot

(3-5)

Where:

- Irw, is the inertia of the reaction wheel, including both the rotor and the wheel,
- ωmotor, is the angular velocity of the motor,
- Irobot, is the inertia of the robot about its vertical axis,
- θ, is the desired rotation angle of the robot,
- trot, is the desired time for the robot to complete the rotation.

The total inertia of the reaction wheel is the sum of the inertias of the wheel and the rotor. The

inertia of the wheel can be estimated using SolidWorks (as shown in Table 3-2), where Iz represents the inertia along the vertical axis, which aligns with the robot’s axis of rotation.

For the rotor, since the value is not in the datasheet, it can be estimated using equation (3-6) if the

mass (M) and radius (R) are known. However, these values are not specified in the datasheet. Given

that the total mass of the motor is 64 g, it is assumed that the rotor’s mass constitutes only a fraction

of this, therefore the rotor’s inertia can be neglected.

Axis | Inertia
Ix | 0.00135 kg⁄m²
Iy | 0.00135 kg⁄m²
Iz | 0.00254 kg⁄m²

Table 3-2 - Inertia Measurements of Wheel

I =

1
2
- M ∙ R

2
(3-6)

Using equation (3-5), and knowing the inertia of both the wheel and the robot, the maximum

angular velocity of the motor required to rotate the robot 360 degrees (2π radians) in 5 seconds can

- 22 -

be calculated as follows:

ωmotor = 2 ∙

Irobot

Irw

∙

θ

trot

= 2 ∙

0.0511
0.00254 ∙

2π
5

= 50.54 rad
s
⁄ | (3-7)

This angular velocity, equivalent to 483 RPM, is well within the capabilities of the motor.

The wheel was intentionally designed with a higher inertia than required to adapt to future projects

where additional components may be added to the robot.

### 3.4 Summary

The chapter provided a detailed explanation of the design and implementation of the reaction wheel

system within the air-bearing floating robot. The CAD model, developed in SolidWorks, was used

not only to calculate the moments of inertia for both the robot and the reaction wheel system, but

also to manufacture the wheel from 316L stainless steel, and any other components needed, such as

the motor base. The spoke structure design of the wheel intentionally reduce weight and maximize

the moment of inertia. Driving this wheel is the GM3506 BLDC motor, selected for its better con-

trollability and performance over traditional brushed DC motors, drives the wheel. The entire

Attitude Control System was centred to the robot’s horizontal plane and aligned with its vertical axis.

Finally, a pair of counterweights was added to shift the centre of mass to the geometrical centre of

the robot.

- 23 -

## 4 ROBOT ATTITUDE DYNAMICS AND CONTROL VIA RE-

## ACTION WHEEL

### 4.1 Introduction

Attitude determination and control is one of the main subsystems in spacecraft. This chapter exam-

ines the principles of attitude control for a floating robot, which simulates a spacecraft, using reaction

wheels. Reaction wheels allow to control precise control of orientation, without the need for external

thrusters, following the principle of conservation of angular momentum, as discussed in Section 2.3.

Moreover, the use of system coordinates is important for attitude determination. The movement

of satellites can be described in different frames, so it is important to clearly define each frame, and

the transformation matrices needed to transition between them. This chapter introduces the concepts

of inertial and rotational frames, along with the various coordinates systems used to describe the

robot’s orientation.

Additionally, the chapter covers the mathematical modelling of the robot’s dynamic behaviour,

including the equations of motion and the reaction wheel model. The control theory required to man-

age the robot’s orientation, and the approach used to verify the performance of the control system,

are also discussed in detail.

### 4.2 Coordinate Frames

This section discusses the coordinate frames used to define the motion and orientation of the air-

bearing floating robot and its subsystems. The primary frames considered are the Granite Table

Frame, the Robot’s Body Frame and the Orbit Frame. Additionally, a Mechanical Frame derived

from the CAD model is used to transfer coordinates between the body frame and the secondary

frames of the robot, including those for the reaction wheel, sensors and Raspberry Pi.

### 4.2.1 Inertial Frame vs Rotational Frame

In orbital mechanics, the absolute acceleration a⃗ of an object’s centre of mass can be measured within

a reference or inertial frame. This reference frame “has neither translational nor rotational accelera-

tion relative to fixed stars” [18] and is governed by Newton’s first law, which states that an object

will remain in its state of motion unless acted upon by an external force. Typically, the inertial refer-

ence frame is usually defined relative to fixed stars or the Earth, but for this project, it is is aligned

with the granite table.

Alternately, the rotational frame does accelerate and rotates relative to the inertial frame. In this

reference fictitious forces appear, such as centrifugal and Coriolis forces [19]. The Transport theorem

links the time derivatives of vectors in rotating and inertial frames and describes how the rotation of

- 24 -

the frame influences the observed motion of the system.

### 4.2.2 Table Frame

The Table Frame functions as the inertial reference for this project. This frame is fixed to the granite

table on which the robot moves. The X-axis aligns with the shorter side of the table, the Y-axis with

the longer side, and the Z-axis points upward, completing the coordinate triad. The origin of this

frame is set at the lower left corner of the table.

### 4.2.3 Body Frame

The body frame is a rotating reference frame attached to the robot and aligned to the robot’s centre

of mass aligned to its principal axis of inertia. This frame describes the robot’s dynamics, as the robot

moves, the axes on the horizontal plane of this frame rotate around the vertical axis, following the

robot’s orientation.

### 4.2.4 Orbit Frame

The orbit frame describes the trajectory of the robot as it moves over the table. This frame tracks the

robot’s path, with its origin is at the robot’s centre of mass. The Z-axis aligned with the table’s Z-axis

and the Y-axis aligned with the direction of the robot’s velocity.

These coordinate frames and their transformations are useful to analyse and control the robot’s

movement and orientation with respect to the granite table. For a more detailed explanation of these

primary frames as well as the secondary frames associated with the reaction wheel, sensors and CAD

reference frame please refer to “APPENDIX A: Coordinate System Definition (CSD) Document”.

### 4.3 Robot Kinematics Equations – Passive Control of Reaction Wheel

Assuming the robot has no translational motion, the angular velocity vector of the robot (body) frame

relative to the table (inertial) frame can be denoted as:

ωb⁄i = pî+ qĵ+ rk̂ | (4-1)

For this project the only rotation is about the vertical axis of the robot, a rotation matrix is Rφ

implemented to describe the rotation over the X-axis of the robot. Since the vertical axis of the robot

(X-axis), is aligned to the Z-axis of the table, an extra -90-degrees rotation matrix Rθ has to be added

to transformation from the body frame to the inertial frame, see equation (4-2).

Rφθ = [

cos θ | 0 sin θ
0 | 1 | 0
− sin θ 0 cos θ

][

1 | 0 | 0
0 cosφ −sinφ
0 sinφ | cosφ
] | (4-2)

The angular velocity ωb⁄i of the body with respect to the inertial frame is then calculated with

equation below:

- 25 -

[

p
q
r

] = [

cos θ | 0 sin θ
0 | 1 | 0
− sin θ 0 cos θ

][

1 | 0 | 0
0 cosφ −sinφ
0 sinφ cosφ

][

φ̇
0
0
] | (4-3)

Substituting θ = 90 degrees in equation (4-3) we can deduce that:
[

p
q
r

] = [

0
0
φ̇
] | (4-4)

This simplifies the equations as the model can be described only using a single angular velocity:

φ̇ = r = ω | (4-5)

From the Euler’s Moment Equations (2.6), applied to a single rotation the rate of change of the

angular momentum of the robot can be defined as:

τ = ω̇ ∙ Jb | (4-6)
Where, Jb = 0.0511 kg m² ⁄ | is the moment of inertia on the vertical axis of the robot.

The state vector x and control variable are defined by:

x = [

φ
ω
] | (4-7)
u = [τ] | (4-8)

Since through the camera and the IMU the position and the angular velocity can be measured, from equations (2.7) and (2.8) we can deduce the matrix A, B and C for the state ẋ = [φ̇ ω̇]

T
:

A = [

0 1
0 0
] | (4-9)

B = [

0
1
Jb

⁄

] | (4-10)

C = [

1 0
0 1
] | (4-11)

### 4.3.1 Controllability of Outer Loop

From equation (2.9) the controllability matrix (Qc ) can be calculated:

Qc = [

0 | 19.5465
19.5465 | 0
] | (4-12)

Because the rank of Qc

, -rank(Qc
) = 2-, is equal to the size of the matrix A from (4-9), the system

is considered as fully controllable.

- 26 -

### 4.3.2 Observability of Outer Loop

Similarly, because the rank of the observability matrix, Qo, calculated from equation(2.10), is

equal to the size of the matrix A; the system is fully observable.

Qo = [

1 0
0 1
0 1
0 0
] | (4-13)

The controllability and observability matrices and ranks can be calculated using the MATLAB

commands “ctrb(A, B);” and “obsv(A,C);”; refer to APPENDIX B: MATLAB Scripts.

The transfer function for the orientation of the satellite, obtained from the state-space representa-

tion is:

φ
τ

=

1
Jb ∙ s

(4.14)

### 4.4 Control Torque with Reaction Wheels in Passive Mode

Once it is stated that the system is controllable and observable, the open-loop poles of the system can

be computed using the determinant in (4-15):

p = det(sI − A) | (4-15)

Then, using the state feedback controller strategy from (2.4.3) new poles can be determined to

stabilize the system for a required time response in closed loop. The values of the matrix K are

equivalent to a proportional, Kp, and derivative, Kd, gains of a controller of the form:

T = Kp

(φerr) + Kdφ̇ | (4-16)

The output of the controller is used as the torque reference for the inner loop.

### 4.5 Reaction Wheel dynamics

### 4.5.1 Motor Electrical & Mechanical Equations

Given the three-phase nature of a BLDC motor, equations that describe the model turn complex, as

shown below:

Va = RaIa + La

dia
dt

+ Mac

dib
dt

+ Mbc

dic
dt

+ ea,

Vb = RbIb + Lb

dib
dt

+ Mac

dia
dt

+ Mbc

dic
dt

+ eb,

Vc = Rc

Ic + Lc

dic
dt

+ Mac

dib
dt

+ Mbc

dic
dt

+ ec
,
| (4-17)

where Va, Vb, and Vc

are the stator phase voltages; R is the resistance per phase, ia, ib and ic are the

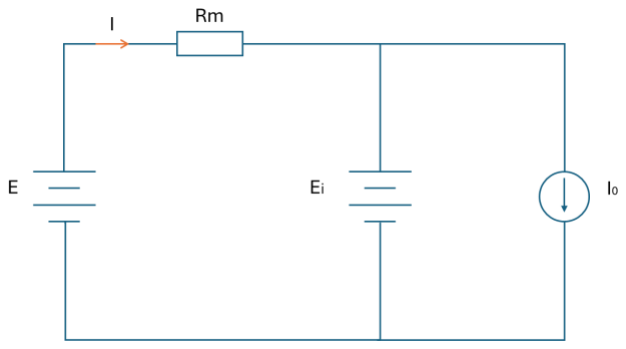
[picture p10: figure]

- 27 -

stator phase currents; La = Lb = Lc are the self-inductances of each phase, and are considered equal

and constant for each phase. Mac and Mbc are the mutual inductances and ea, eb and ec are the back

electromotive forces. The Back EMF is trapezoidal and is a function of the rotor speed ω, and posi-

tion θ:

ea = fa

(θ)λω,

eb = fb

(θ)λω,

ec = fc

(θ)λω,

(4-18)

where λ, is the total flux linkage. The total electromotive torque Te , in [Nm] can be represented as a

function of all phases:

Te =

eaIa + ebIb + ec

Ic
ω
. | (4-19)

Or by:

Te − TL = J

dωm
dt + Bωm. | (4-20)

However, this type of model requires to adapt an extra three-phase invertor, which complicates

modelling the plant. An C.O.T.S. Electronic Speed Controller, (ESC), which applies a Sensorless

Control of BLDC Motors Technique through reading the back-EMF, is used for this the motor model

and therefore it can be simplified to a Three constant motor model DC (See Figure 4-1) [21].

### 4.5.2 Three-Constant motor model DC representation

In literature there exist several models of BLDC motors, but one of the most common is the Three-

Constant BLDC motor model, which is a normal DC representation of the brushless motor, using

only three of its parameters.

Figure 4-1 – Three-constant motor model DC representation of a three-phase motor.

The three constants are the speed constant KV, the motor resistance Rm, and the no load current

I0. Alternately to the speed constant, some authors use the torque constant Kt
. Inductances are not

used in this model as the dynamics of the electronic part of the loop is much faster than the

- 28 -

electromechanical dynamics. In general, the electronic part settles approximately ten times faster

than the mechanical part.

This model allows to rewrite equations (4-25), (4-27) and (4-20) as:
e = Keω, | (4-21)
E = V = Ri + Keω, | (4-22)

T = Kt

i, | (4-23)

Jω̇ + bω = Kt

i, | (4-24)

where Ke=Kt. Considering that ω is the angular velocity of the wheel with respect of the satellite,

plant can be modelled on block diagram, as in Figure 4-2 and the transfer function that takes the rate

of change of the angular momentum as a function of the input voltages can be calculated.

Figure 4-2 - Momentum exchange devise model.

Figure 4-2 denotes the basic model of a moment exchange device, Jw and Js are the moment of

inertia of the reaction wheel and the spacecraft, in this case the robot. ωREL is the angular velocity of

the reaction wheel relative to the robot and b is the damping friction coefficient. In this model V is

the input voltage of the motor.

Since no external disturbances, Td, are affecting the system, the main relation between the reac-

tion wheel and a satellite, or in this case the robot, is defined by the Euler’s moment equation of

angular motion:

ḣ

S + ḣw = 0 | (4-25)

To apply a torque on the body, the motor must produce a torque in the opposite direction:

ḣ

S = −ḣw | (4-26)

Therefore, from Figure 4-2 and equations (4-25) and (4-26) the transfer function that relates the

rate of change of the angular momentum of the reaction wheel, and the voltage of the motor can be

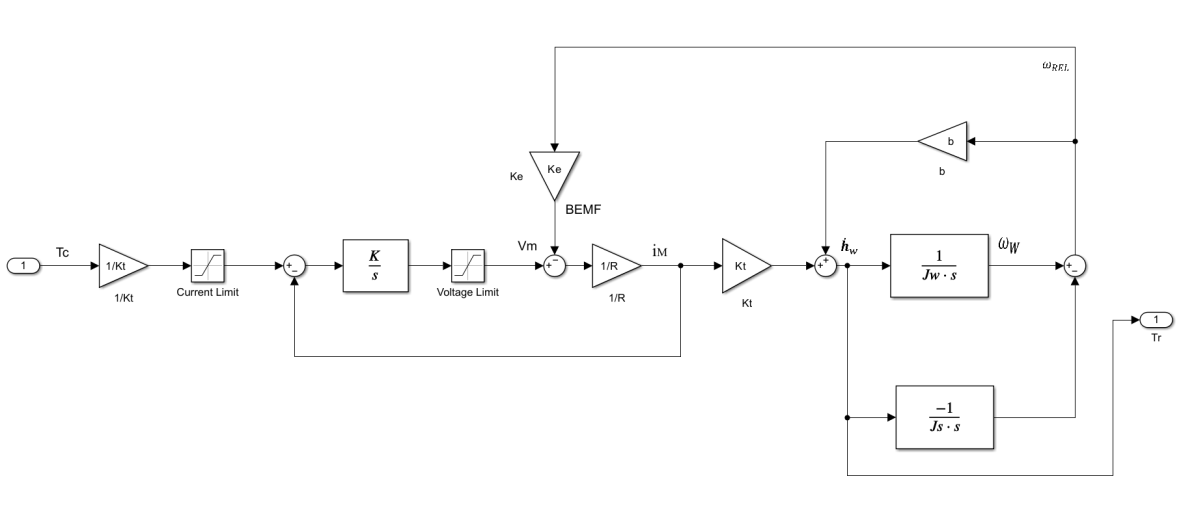
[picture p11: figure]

- 29 -

defined as:

ℎ̇w
V

=

Iwω̇w
V

=

s (

KM
RM

)

s + (

1
Iw

+

1
IS

) (

KVKM
RM

+ B)

(4-27)

The output of equation above is the rate of change of the angular momentum, equivalent to the

torque. However, the input from the outer controller is also torque so the transfer function from (4-27) must be updated converting the torque ḣw a response of a command Tc
. Figure 4-3 shows the block

diagram of a reaction wheel in torque mode [5].

Figure 4-3 - Reaction Wheel in torque mode.

Additionally, it is possible to neglect the viscosity damping coefficient, b, as it is several orders

of magnitude smaller than the other variables. Considering also that the inertia of the Robot is more

than 20 times bigger than the one from the wheel, the modified transfer function that relates the

commanded and reaction torques, with an integral gain to control the voltage according to a desired

torque, according to Figure 4-3:

Tr
Tc

=

ḣw
Tc

=

K
s ∙ R

⁄

1 +

K
s ∙ R

(1 +

Ke ∙ Kt
K ∙ Jw

)

(4-28)

Notice that Figure 4-3 adds a feedback path from the motor current, as it is proportional to the

electrical torque produced by the motor. A gain K, is also added before the voltage input. If that gain

K, is set that

K ≫

Ke

- Kt
Jw

(4-29)

So that the term in the parenthesis at equation (4-28) has a value of ~1. Equation (4-28) can then

be rewritten as in (4-30), a first-order equation with a time constant depending on the resistance of

- 30 -

the motor.

ḣw
Tc

=

1
1 + s(R
K

⁄ )

(4-30)

From the simplified transfer function, it was verified that the system is observable and controlla-

ble through a state-space representation using MATLAB.

### 4.6 Summary of Mathematical Developments

This chapter provided a detailed description of the kinematic and dynamic equations for attitude

control using reaction wheels. It demonstrated how the relationships between various reference

frames—such as the body and inertial frames—can be mathematically manipulated to measure and

control the robot’s angular velocity. The use of transformation matrices between these frames was

essential in defining the robot’s orientation and movement.

Additionally, important control concepts like observability, and controllability, were introduced

for the passive attitude control system. The chapter explained how control strategies, such as full-

state feedback and pole placement, were applied to stabilize the system in a closed-loop configura-

tion. The analysis of the system's step response and pole locations helped to obtain the gains for the

correct control of the system.

A simplified model of reaction wheels driven by brushless motors was also discussed, demon-

strating their effectiveness in stabilizing the system. In conclusion, reaction wheels, combined with

appropriate mathematical models and control strategies, provided the necessary stability and preci-

sion for controlling the robot’s orientation.

## 5 NUMERICAL SIMULATIONS IN SIMULINK

### 5.1 Introduction

This chapter presents the simulations conducted in Simulink and MATLAB to validate the control

design for the reaction wheel system of the air-bearing floating robot. The control architecture in-

cludes both an inner and an outer loop, where the inner loop focuses on controlling the reaction

wheel’s torque and the outer loop controls the robot’s attitude. The simulations evaluate the system’s

response to different inputs, ensuring that the desired orientation is achieved while considering the

physical limitations of the motor, such as maximum torque and angular velocity.

Through a tuning process of the controller gains (Kp and Kp), the behaviour of the system can be

improved to minimize overshoot, reduce settling time, and ensure a smooth and stable response. The

chapter explores various pole placements and optimization technique, discussed in the previous chap-

ter, and compares different sets of gains to achieve optimal performance. The effectiveness of the

- 31 -

controller is analysed through step responses of the system, along with the torque and angular veloc-

ity responses of both the reaction wheel and the robot. These simulations show how the system

behaves under different scenarios and how control parameters can be adjusted to meet the project’s

requirements. All Simulink Models can be found in APPENDIX B: MATLAB Scripts & Simulink

Models.

### 5.2 Simulink Models

### 5.2.1 Outer Loop

Through some block algebra, the block representation of the outer loop, based on Figure 2-2, is

modelled in Figure 5-1. Here, Kp and Kd correspond to the values from the torque control (4-16).

The open loop has both poles at zero (5-1). This indicates that the system behaves as a double inte-

grator, which means it is marginally stable. While it does not diverge exponentially, a constant input

will make the output grow indefinitely (see Figure 5-2).

Figure 5-1 - Outer Loop - Robot Attitude Control

s1,2 = 0 | (5-1)

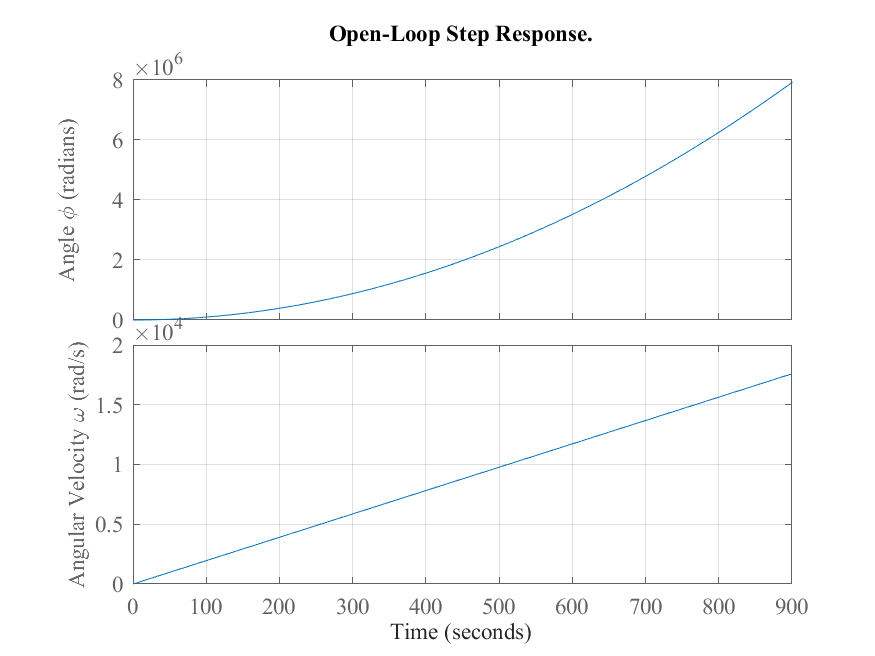
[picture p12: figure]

- 32 -

Figure 5-2 - Open-Loop Step Response of Attitude Control

Different pole pairs were tested. Although poles placed farther from the imaginary axis achieve

faster response times [20], the desired real poles were chosen not far from the axis, to prevent the

system from significantly lowering its steady-state gain. Figure 5-3 shows the step response for dif-

ferent pole pairs. For each pair of poles, a matrix K was computed using a MATLAB script

(APPENDIX B: MATLAB Scripts).

The new poles selected for the system (see Figure 5-4), through optimization where:

p = [−4.89, −3.998] | (5-2)

- 33 -

Figure 5-3 - Step Response for different Poles.

Figure 5-4 – Poles location using Full-State Feedback Control, P1(-4.89,0), P2(-3.998,0).

The matrix K that stabilizes the system with these poles is defined as follows:

K = [1.0002 0.4547] | (5-3)

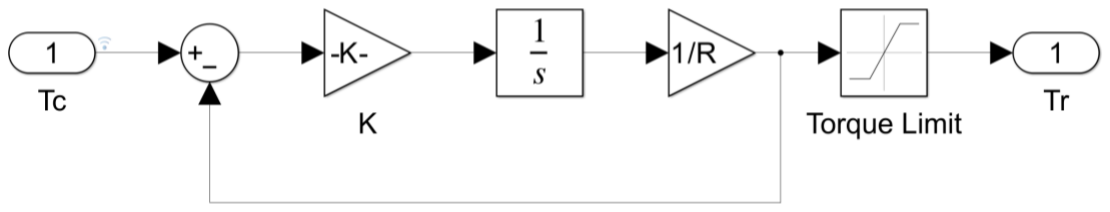
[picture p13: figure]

- 34 -

Figure 5-5 shows the response for orientation and angular velocity based on the selected poles.

Figure 5-5 - Closed Loop Step Response of State Feedback Controller.

### 5.2.2 Inner Loop

Figure 5-6 shows the simplified model of a reaction wheel based on the transfer function derived in

Equation (4-30). The torque limit is set to 80% the maximum torque provided by the motor to prevent

saturation. However, this limit can be adjusted to ensure the motor operates within safe torque limits.

The Gain K is calculated by substituting Equation (4-29) with the parameters from Table 5-1, the

gain then should have a value higher than 1.7938.

Figure 5-6 -Simplified Torque Mode of a Reaction Wheel.

- 35 -
Parameter | Value | Unit
Ke | 0.06754 | V*s/rad
Kt | 0.06754 | Nm/A
R | 5.6 | Ohms
Jw | 0.00254 | Kg*m^2
Js | 0.05116 | Kg*m^2

Table 5-1 – Reaction Wheel Mechanical Parameters

The inner loop must be at least ten times faster than the outer loop, so that the outer loop gains

calculated from the passive control of the reaction wheel could be valid in an active control of the

wheel. The K value was chosen, through Simulink, to achieve a settling time of Ts = 0.001 s, with

an undershoot of Q ≤ 5%. The resultant value of K and the parameters for the step response are

shown in Table 5-2. Figure 5-7 presents the step response of the plant. The farther location of the

pole from the imaginary axis, at p = −2000 as shown in Figure 5-8, confirms the faster response of

the motor system,

Parameter | Value
Gain K | 11200
Rise Time | 0.0011 seconds
Settling Time | 0.00196 seconds
Overshoot | 0 %

Table 5-2 - Step Response Parameters for K=11200.

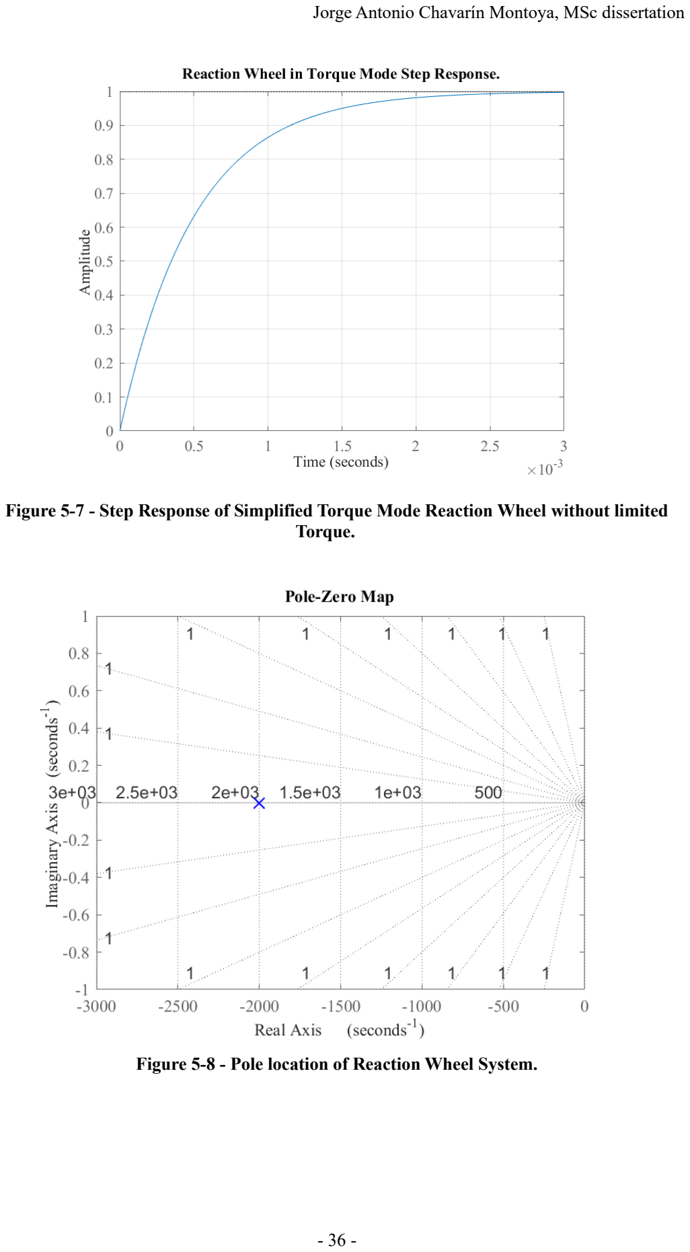
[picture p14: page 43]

- 36 -

Figure 5-7 - Step Response of Simplified Torque Mode Reaction Wheel without limited Torque.

Figure 5-8 - Pole location of Reaction Wheel System.

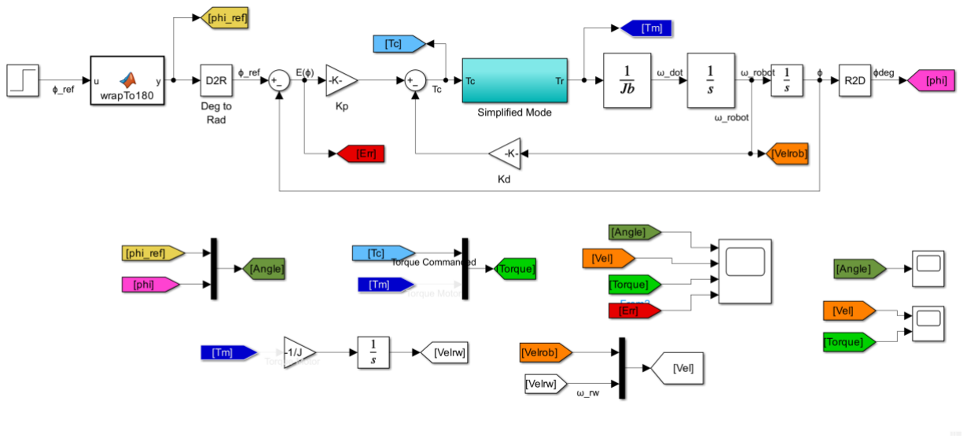
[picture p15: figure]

- 37 -

### 5.3 Numerical Experiments

In complete control loop is showed in Figure 5-9, the simplified mode corresponds to the reaction

wheel inner loop. The control law works perfectly for small angles, where φ ≈ 0, see Figure 5-10,

making it ideal for stabilization due to the simplicity of the equations. However, for large manoeu-

vres, due to the motor’s physical limitations (voltage, current, torque, etc…), the response overshoot

increases. The Feedback Controller does not account for these limitations. To address this, the first

solution was to bound the angle setpoint to −180 deg ≤ φ ≤ 180 deg, as the objective is to rotate

the robot to a desired orientation, not to perform continuous rotations. However, for higher setpoints,

for example 170 degrees, a ~27% overshoot was observed (Figure 5-11). Through further optimiza-

tion, new values for Kp and Kd were obtained for the matrix K:

K = [0.9 1] | (5-4)

Figure 5-9 - Complete Robot Attitude Controller.

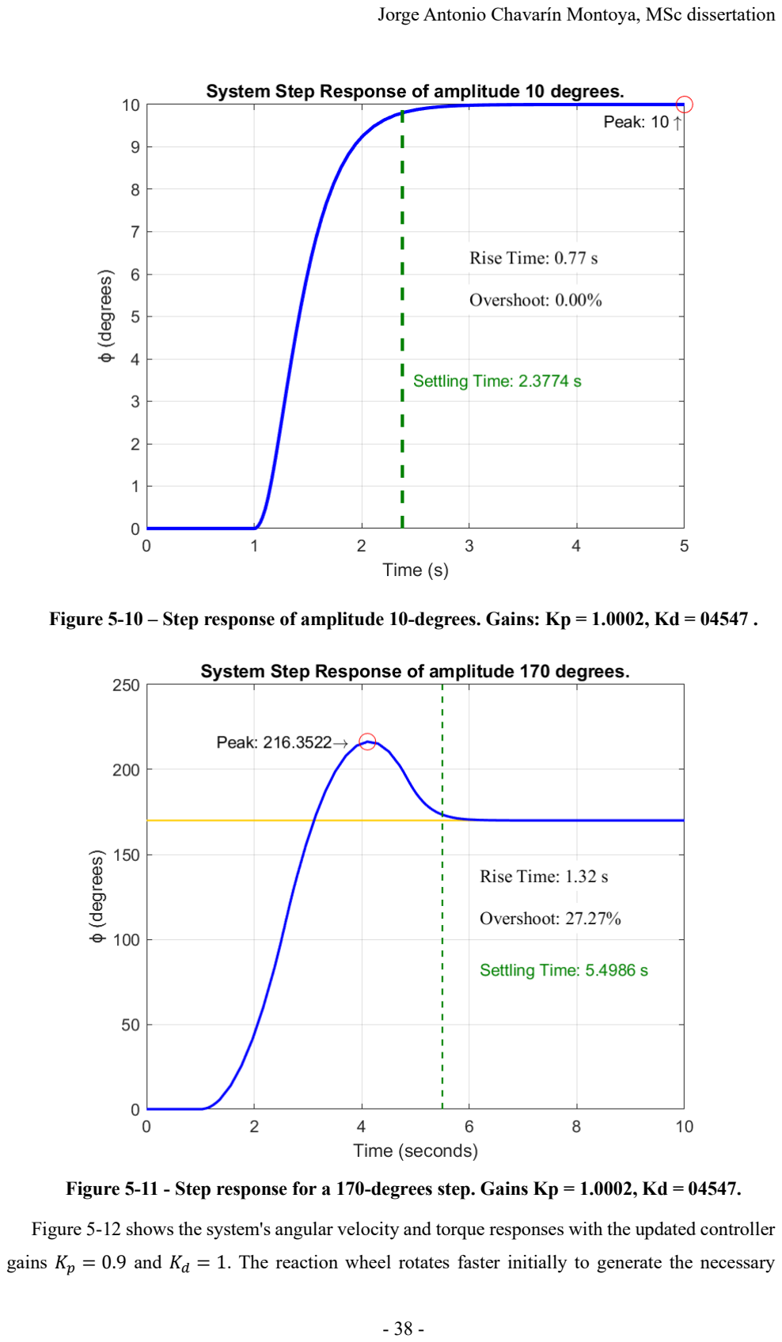
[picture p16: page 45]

- 38 -

Figure 5-10 – Step response of amplitude 10-degrees. Gains: Kp = 1.0002, Kd = 04547 .

Figure 5-11 - Step response for a 170-degrees step. Gains Kp = 1.0002, Kd = 04547.

Figure 5-12 shows the system's angular velocity and torque responses with the updated controller

gains Kp = 0.9 and Kd = 1. The reaction wheel rotates faster initially to generate the necessary

- 39 -

torque to rotate the robot to the desired orientation. In the bottom graph, the blue line represents the

torque commanded by the outer loop controller, while the orange line shows the torque produced by

the reaction wheel. The actual torque output is significantly lower due to the physical limitations of

the motor. The motor reaches its maximum torque capacity and remains saturated for a brief period,

as seen in the plot. It is important to note that, although the torque commanded, and the torque gen-

erated by the reaction wheel are opposite in nature, the reaction torque plotted is the rate of change

of the angular momentum of the robot.

Figure 5-12 – Top: Comparison between the angular velocity of the robot and the reaction wheel. Bottom: Commanded torque vs actual torque reaction of the robot.

Although, the updated controller gains Kp = 0.9 and Kd = 1 result in a slower system response

(Figure 5-13), with a settling time of 5.8 seconds, the response is noticeably smoother compared to

previous configurations. The system now exhibits a rise time of 2.53 seconds and, mor importantly,

no overshoot, which indicates improved stability. This smooth response confirms that the system

reaches the desired setpoint without exceeding it. While the response is slower, the absence of oscil-

lations and overshoot demonstratesthe trade-off made between speed and stability. The updated gains

result in a well-controlled response that is more appropriate for the sensitive manoeuvres required by

the reaction wheel system.

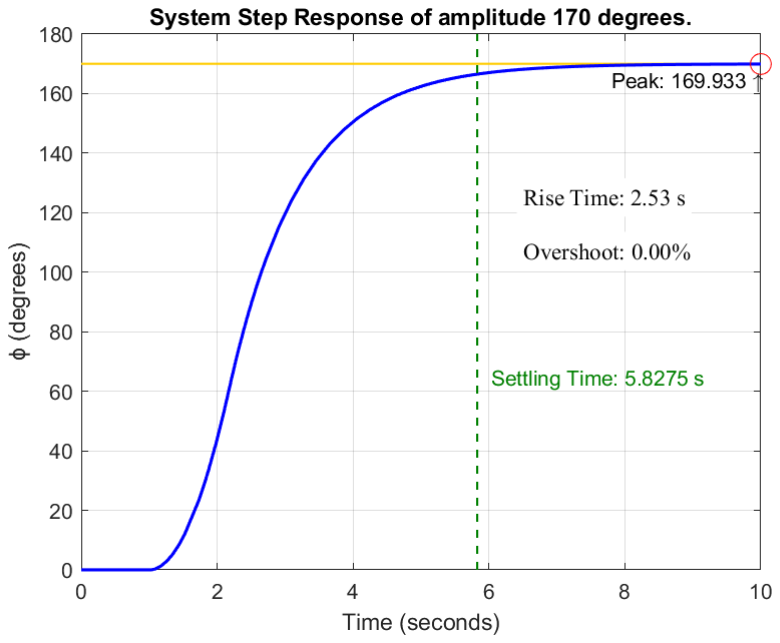
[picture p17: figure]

- 40 -

Figure 5-13 – Plant Step response of amplitude 170 (deg.). Gains Kp = 0.9 & Kd = 1.

### 5.4 Summary

In this chapter, the reaction wheel system’s numerical simulations were performed to evaluate its

performance in rotating a floating robot. Different control strategies were tested, and controller gains

were adjusted to improve the system’s response to step inputs. The results indicate that while the

initial configuration of gains, calculated through a feedback controller strategy that did not consider

the mechanical limitations of the motor and assumed passive control of the reaction wheel, produced

overshoot and oscillations when implementing an active control, the optimized gains of Kp = 0.9

and Kd = 1 provided a more stable and smoother response. The system reached the desired orienta-

tion without overshooting, and although the settling time was slightly longer, it was still in an

acceptable range. However, the reaction wheel’s torque was limited by the motor’s mechanical and

electrical constraints, but the latter simulations considered these limitations.

The results demonstrate the effectiveness of the full-state feedback control even when considering

the passive behaviour of the reaction wheel. Nevertheless, extra tuning had to be performed to ac-

count for the system’s physical limitations. By adjusting carefully the control gains, the system was

able to balance the performance and the physical restrictions, leading to a stable, smooth, and effi-

cient attitude control system. These simulations provide a reliable approach for validating control

laws applied to the reaction wheel system and ensure that the system can meet operational require-

ments for future space systems testing.

- 41 -

## 6 CONCLUSION

This dissertation presents the design and implementation of an Attitude Control system (ACS) using

a single-degree-of-freedom Reaction Wheel for an air-bearing floating robot. The system was de-

signed to allow the robot to change its orientation based on a user input, simulating the n microgravity

conditions found in space. The project covered various aspects, from mechanical design and CAD

modelling to control algorithms and Software-in-the-Loop (SIL) testing, resulting in a system that

meets the project’s objectives.

The development of the reaction wheel system, which generates enough torque to control the

robot’s attitude, was a major achievement in this project. The integration with SIL testing allowed

for real-time verification and adjustments of the control algorithms, showing that the system could

reorientate to a desired angle. Some challenges were encountered, such as hardware limitations and

difficulties in tunning the control due to unavailable motor parameters not provided from the manu-

facturer, but the system still showed stable and accurate results in the simulations.

The CAD process was important to make sure all components fit and worked together within the

floating robot, to obtain the robots parameters such as centre of mass location, moments of inertia

and weight of the robot. These values were useful for designing the wheel. and for calculating the

rotating matrices to convert between different coordinate systems.

The real robot was not symmetric as it had components mounted in different parts of the main

frame. As a result, the centre of mass and the principal axes of inertia were not aligned with the

geometric centre, which made the robot to rotate in a way that wasn’t aligned with its principal axes

of inertia. This added complexity to the mathematical modelling of the system. To correct this, coun-

terweights were added to align the motor’s axis properly.

The control law was divided into two parts: an outer loop and an inner loop. The two-loop system

was used to separate the motor control from the rest of the satellite. The reaction wheel system was

treated as an independent subsystem. The outer loop controlled the robot’s attitude along one axis

and was designed using a full-state feedback controller (pole placement strategy). Initially, the reac-

tion wheel was treated as passive (a gain of 1), and the control law was based on a proportional-

derivative equation, T = Kp

(φerr) − Kdφ̇
, here the angle error and angular velocity of the robot

multiplied by specific gains provided the torque input for the inner loop. However, this strategy did

not contemplate the mechanical limitations of the motor plant, making the response to produce an

overshoot and to oscillate as the desired angle increased. Further adjustments to the outer loop gains

were made considering the motor’s physical limitations, such as voltage, current and torque, once

the inner loop was designed.

The inner loop simulated the behaviour of the motor, which was a three-phase BLDC motor. Since

- 42 -

the manufacturer did not provide many motor parameters, a simplified three-constant DC model rep-

resentation was used instead. After determining the transfer function of the system and through some

block algebra, an integral gain was calculated to make the system respond like a first-order plant,

adjusting the torque based on a commanded input (the control signal from the outer loop). The inner

loop needed to respond at least 10 times faster than the outer loop, so the motor’s response time was

optimized based on settling time and undershoot requirements. In this simulation, the motor’s phys-

ical limitations, such as voltage, current, and torque, were considered.

In conclusion, this project shows how reaction wheels can be applied to control small satellited

and robotic platforms. The work done here shows that the control system is effective in controlling

the robot’s orientation in a simulated environment. The results open possibilities for future work,

such as improving the hardware, upgrade the control strategy to make the robot to reorientate while

translating over the table or design different control laws using the full three-phase design of the

motor.

### 6.1 Evaluation

This project aimed to achieve three main objectives, explained in section 1.2, all of which were suc-

cessfully completed through simulations, despite delays in receiving the physical components. The

first objective was to create a detailed CAD design of the air-bearing robot with a Reaction Wheel

assembly. The CAD design was done in SolidWorks, and all the necessary components were sized

and included following the CubeSat standard of modularization of subsystems to allow for attitude

control experiments. This model included, apart from the main robot frame, different components

such as a LiPo battery, a Raspberry Pi, an IMU, and a camera module. Even though the wheel was

slightly oversized, the motor was still available to spin with the wheel mounted; this will allow future

projects to add components to the robot without redesigning the wheel.

The second objective focused on developing a PID controller. This goal was achieved through

describing the system mathematically and modelling it in Simulink. It was divided into two loops,

the outer loop was designed as a PD controller while the inner loop incorporated and Integral gain to

stabilize the plant.

The third objective was for the robot reorient itself based on user-commanded attitude settings.

Although initially the objective was to develop the physical system and do physical tests, due to the

delays in receiving the components the goal was modified to achieve it in Simulations. In that way,

the goal was accomplished as the plant responded accurately to input commands, showing that the

system could perform the required attitude adjustments in real life.

In summary, all project goals were met through simulations and CAD modelling, despite the ab-

sence of physical testing due to component delays. The simulations allowed to completely validate

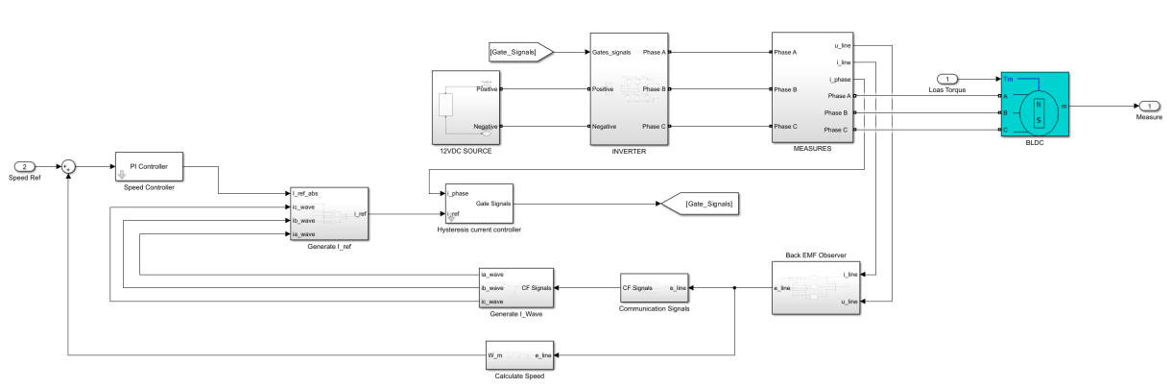
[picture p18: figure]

- 43 -

the system, showing that the Attitude Control system, worked as expected in a virtual environment.

### 6.2 Future Work

The next step in this project will involve incorporating the physical components into the existing

model and conducting physical tests. This includes integrating the PWM-controlled brushless DC

motors. Performing these physical tests will provide a more accurate evaluation of the system’s per-

formance and will help to identify any adjustments needed for space applications.

### 6.2.1 PWM Implementation for BLDC Motors

Implementing a Pulse Width Modulation (PWM) control involves measuring certain parameters from

the motor that are not provided by the manufacturer, such as self and mutual inductances, and using

a three-phase invertor, or in this case, an Electronic Speed Controller (ESC) unit. The ESC regulates

the speed and torque of BLDC motors through PWM by controlling the amount of voltage applied

over time. Despite limited documentation on ESC modules, it has been proven that they can achieve

performance levels above 95%, making them ideal for this application, where the inner loop needs

to be as fast and precise as possible. Another thing to consider is that not all ESC modules are bidi-

rectional and would only control the motor speed on one direction. Figure 6-1 shows a PWM

controller of a BLDC motor. Although this controller design was initially proposed, due to the lack

of parameters available of the motor and no form of measuring them a simplified DC representation

was implemented.

Figure 6-1 - PWM Sensorless Controller of a BLDC motor.

### 6.2.2 No Body and Axis of Inertia Alignment

Another issue identified is the misalignment between the robot’s body and its principal axes of iner-

tia. Since the robot’s components are not symmetrically distributed, the centre of mass and the axes

of inertia do not align with the geometric centre. This leads to undesired rotational behaviour that

complicates the control system. To correct this, counterweights were added to align the robot’s prin-

cipal axis of inertia, with the rest of the frames. However, further work will be needed to study the

- 44 -

effects of this misalignment in real-world conditions, especially once the physical components are

fully integrated.

## 7 REFERENCES

[1] Schwartz, J. L., Peck, M. A., & Hall, C.D. Historical Review of Air-Bearing Spacecraft Simu-

lators, Journal of Guidance, Control, and Dynamics, 26(4), 513-522. July-August 2003. DOI:

10.2514/2.5085.

[2] Selection of Electric Motors for Aerospace application, Lesson Number 893. MSFC, NASA

Public Lessons Learned System, https://llis.nasa.gov/lesson/893, February 1999.

[3] Rasmussen, R.E. Air Bearing Based Satellite Attitude Dynamics Simulator for Control Software

Research and Development, Calhoun, Institutional Archive of the Naval Postgraduate School.

2001.

[4] Robotic arm reaching for air-bearing platform. ESA Agency. https://www.esa.int/ESA_Multi-

media/Images/2015/12/Robotic_arm_reaching_for_air-bearing_platform, (https://www.esa.int/ESA_Multimedia/Images/2015/12/Robotic_arm_reaching_for_air-bearing_platform) December 2015.

[5] Sidi, M. Spacecrafts Dynamics & Control: A Practical Engineering Approach, Cambridge:

Cambridge University Press, 2000.

[6] Wertz, J., R. Spacecraft Attitude Determination and Control, first Edition, D. Reidel Publishing

Company, Dordrecht, Holland, 1978. DOI: https://doi.org/10.1007/978-94-009-9907-7.

[7] Jovanovic, et al. Design and Testing of a Low-cost, Open source, 3-D Printed Air-Bearing-Based

Attitude Simulator for CubeSat Satellites, Journal of Small Satellites, 8(2):859:880, January

2019.

[8] Fleming, A. et al. Minimum-time Reorientation of a Rigid Body, Journal of Guidance, Control

and Dynamics, 23(1), January-February 2010. DOI: 10.2514/1.43549.

[9] Weston, S, editor. Small Spacecraft Technology. State of the Art Report. Small Spacecraft Sys-

tems Virtual Institute, NASA, California, 2023.

[10] Krishna, N. et al. Design and Implementation of a Reaction Wheel System for CubeSats, IEEE

Xplore, Manipal, India. 2018.

[11] K. Ogata, “Modern Control Engineering”, Fifth Edition. Pearson Education International, Ma-

drid, 2010.

[12] 16.31 Feedback Control Systems, Topic 11: Full-State Feedback Control. MIT Open-
CourseWare, | https://ocw.mit.edu/courses/16-30-feedback-control-systems-fall-

2010/c553561f63feaa6173e31994f45f0c60_MIT16_30F10_lec11.pdf, (https://ocw.mit.edu/courses/16-30-feedback-control-systems-fall-2010/c553561f63feaa6173e31994f45f0c60_MIT16_30F10_lec11.pdf) 2010.

[13] Are brushed motors suitable for industrial applications. Linear Motion Tips, https://www.linear-

motiontips.com/are-brushed-motors-suitable-for-industrial-applications/. (https://www.linearmotiontips.com/are-brushed-motors-suitable-for-industrial-applications/)

[14] Brushed | DC | Motors | Vs. | Brushless | DC | Motors. | Hare | Data | Electronics,

- 45 -

https://www.haredataelectronics.co.uk/brushed-dc-motors-vs-brushless-dc-motors, July 2020.

[15] Krause, P. et al. Analysis of Electric Machinery and Drive Systems, IEEE, pp. 557-601. DOI:

10.1109/9780470544167.ch15.

[16] Hanselman, D. Brushless Permanent Magnet Motor Design, Second Edition. Magna Physics

Publishing, Ohio, U.S.A, 2006.

[17] iPower Moto GM3506 Brushless Gimbal Motor w/ AS5048A Encoder. RobotShop,

https://uk.robotshop.com/products/ipower-motor-gm3506-brushless-gimbal-motor-w-as5048a-

encoder. (https://uk.robotshop.com/products/ipower-motor-gm3506-brushless-gimbal-motor-w-as5048a-encoder)

[18] Curtis, H. Orbital Mechanics for Engineering Students, Butterworth-Heinemann, 2014. DOI:

https://doi-org.surrey.idm.oclc.org/10.1016/C2011-0-69685-1.

[19] Orbital Mechanics & Astrodynamics. Bryan weber, https://orbital-mechanics.space/in-

tro.html,June (https://orbital-mechanics.space/intro.html,June) 2024.

[20] Place: Pole Placement Design. MathWorks, Help Center, https://uk.mathworks.com/help/con-

trol/ref/place.html#mw_00c2ad51-c4f9-46ce-9af1-9465ecfe2af6. (https://uk.mathworks.com/help/control/ref/place.html#mw_00c2ad51-c4f9-46ce-9af1-9465ecfe2af6)

[21] Green, C. and McDonald, R. Modeling and Test of the Efficiency of Electronic speed controllers

for Brushless DC Motors, Session: Transformational Flight – Electric Propulsion, AIAA 2015-

3191, June 2015. DOI: https://doi.org/10.2514/6.2015-3191.

[22] Sidi, M. Spacecraft dynamics and control: a practical engineering approach, Eight Edition,

MLA, Cambridge University Press, 1997.

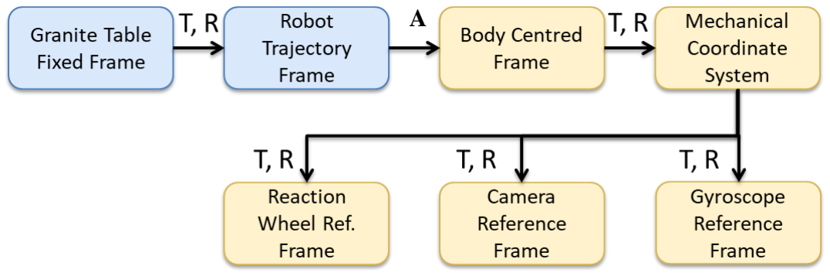
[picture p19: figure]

- 46 -

## 8 APPENDIX

### 8.1 APPENDIX A: Coordinate System Definition (CSD) Document

Figure 8-1: Right hand Rule.

### 1. Overview of Coordinate Systems

1.1 Summary

Table 1: Summary of coordinate systems.

Title | Mnemonic | ID

Flight/Astronomical Frames

Granite Table Inertial Coordinate System | GTI | F-01
Robot Trajectory System (Robot Orbital Frame) | RTS | F-02

Mechanical

Body Centred Reference Frame | BFR | M-01
Mechanical Reference Frame (CAD) | CAD | M-02
Reaction Wheel Frame | RWF | M-B-01
Camera Reference Frame | CAM | M-B-02
Inertial Sensor Reference Frame | IMU | M-B-03

1.2 Frank Diagram

Figure 8-2. Frank Diagram. “T” stands for translation, “R” for rotation and “A” refers to the Attitude Dynamics equations.

- 47 -

### 2. Coordinate Systems

2.1 Attitude Reference Frames

### 2.1.1 Table Fixed Coordinate System

Table 2: RCF Definition

Type | Title | Mnemonic | ID
Fixed | Granite Table Inertial Coordi-nate System | GTI | F-01

Definition:

+X_GTI | The X axis is aligned to the nearest short axis of table. Pointing to the right.
+Y_GTI | The Y axis is aligned to the left long axis of the table.
+Z_GTI | Completes the triad (90 deg). The positive direction is away from the surface of the Earth. (Points to the roof).
Origin | Left front corner of the room.

Rationale: The orbit of the robot is defined and calculated in the GTI frame.

Transformation: -

Translation: -

Rotation: -

Order: -

Comments

Formula: -

Diagram:

Figure 8-3: GTS reference frame.

### 2.1.2 Robot Trajectory Coordinate System (Robot Orbital Frame)

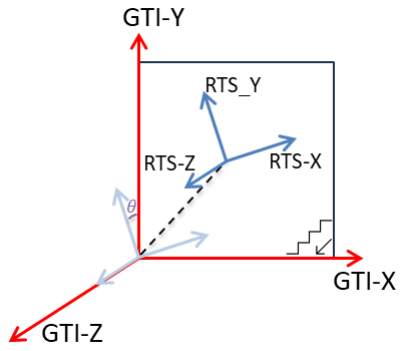
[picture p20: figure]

- 48 -

Table 3: RTS definition

Type | Title | Mnemonic | ID
Translational Frame | Robot Trajectory Coordinate Sys-tem | RTS | F-02

Definition:

+X_RTS | Completes the triad (90 deg).
+Y_RTS | The Y axis pointing to the velocity direction of the robot.
+Z_RTS | The Z-axis is aligned to the Z-axis of the Table Frame.
Origin | Centre of mass of the Robot

Rationale:

Transformation: - Granite Table Inertial Coordinate System (GCI)

Translation: - Translation along X and Y axis.

Rotation: - Rotation about Z axis through a variable angle. Through an angle equal to the angle

between +GTI_Y and the velocity trajectory.

Order: -

Comments: W in Translation matrix is the distance from the base of the Granite Table to the centre

of mass of the Robot in the RTS_Z axis.

Formula: -
[

X
Y
Z

]

RTS

= [

cos θ sin θ 0
− sin θ cos θ 0
0 | 0 | 1

][

x
y
z

]

GTI

Rotation
+ [

x′
y′
W

]

GTI

Translation

Diagram:

Figure 8-4: RTS Reference Frame.

- 49 -

2.2 Mechanical Frames

### 2.2.1 Body-fixed Reference Frame

Table 4: Body-Fixed Frame definition

Type | Title | Mnemonic | ID
Rotating Reference Frame | Body-fixed Reference Frame | BFR | M-01

Definition:

+X_BFR | The X axis points UP, where the minimum Moment of Inertia re-lies.
+Y_BFR | The Y axis points to the FRONT side of the robot.
+Z_BFR | The Z axis completes the triad.
Origin | Centre of mass of the robot.

Rationale: This frame rotates along with the robot. Attitude Matrix describe the position of the

body frame in the room. The actual vertical distance from the table and the Centre of Mass of the

robot is W=0.1344 meters, but it could vary if extra components are added and therefore the po-

sition of the Centre of Mass change.

The following matrices are the DCM and Translation matrixes from the Mechanical Frame to

the Body Frame.

Transformation: From Mechanical Frame to Body Frame.

Translation: Translation along the three axes: [0.0190809 0.00224927 0.10277103]

T

Rotation: Rotation about 3 axes from Mechanical Frame to Body Frame:
[BM] = [
−0.00441177 | 0.97219108 | 0.23414747
−0.00288917 −0.23416116 0.97219350 0.99998609 −0.00361260 0.00384189

]

Order: -

Comments:

Formula:
[

X
Y
Z

]

MNT

= | [
−0.00441177 | 0.97219108 | 0.23414747
−0.00288917 −0.23416116 0.97219350 0.99998609 −0.00361260 0.00384189

] [

X
Y
Z

]

CAD

+ [

0.0190809
0.00224927
0.10277103

]

Diagram:

- 50 -

Figure 8-5. Body Fixed Reference Frame & Mechanical CAD Frame Below.

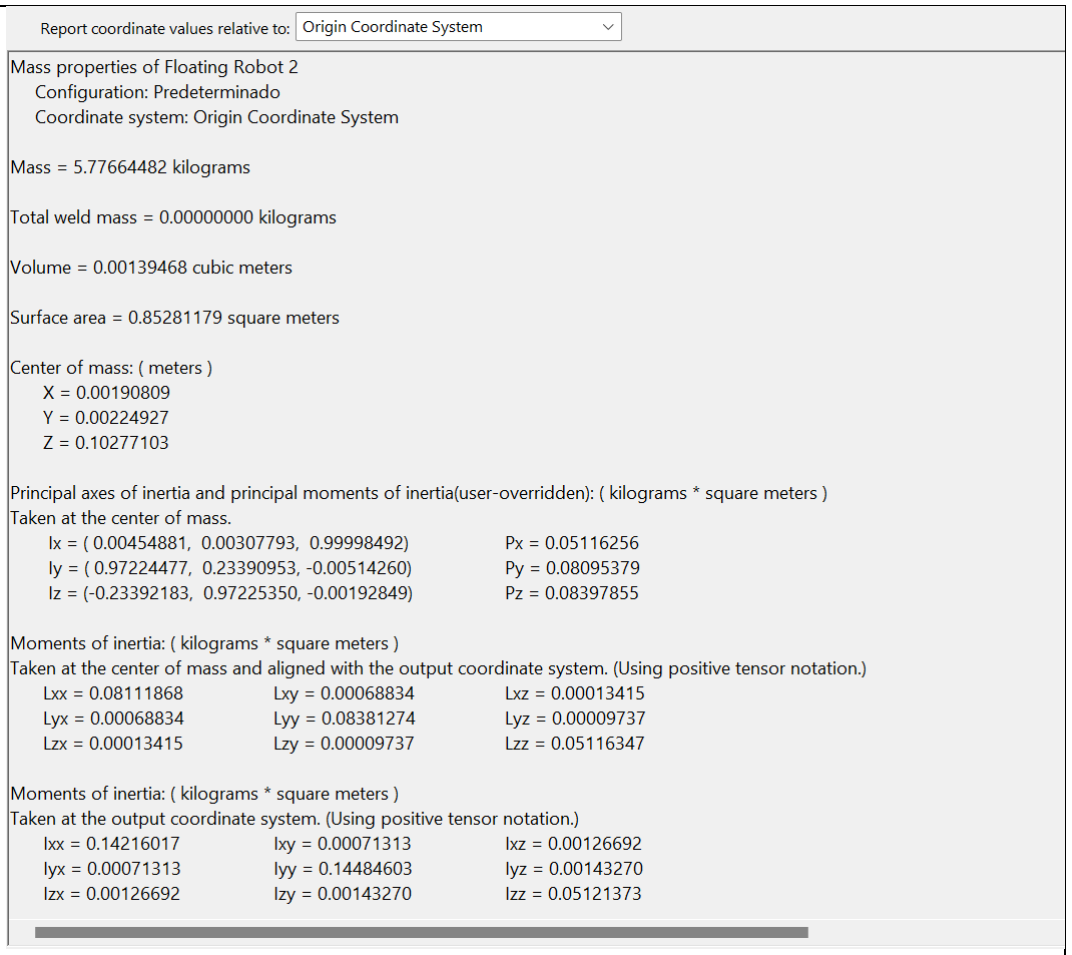
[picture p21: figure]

- 51 -

### 2.2.2 Mechanical CAD Reference Frame

Table 8-5: CAD Reference Frame definition.

Type | Title | Mnemonic | ID
Rotating Reference Frame | Mechanical Reference Frame | CAD | M-02

Definition:

+X_CAD | The X axis points to the RIGHT side of the robot.
+Y_CAD | The Y axis complete the triad.
+Z_CAD | The Z axis points UP, away from the surface of the table.
Origin | Origin of CAD File (0,0,0)

Rationale: This Frame is used to locate the subsequent frames from the Body-Fixed Frame in

the 3D CAD model.

Transformation:

Translation:

Rotation:

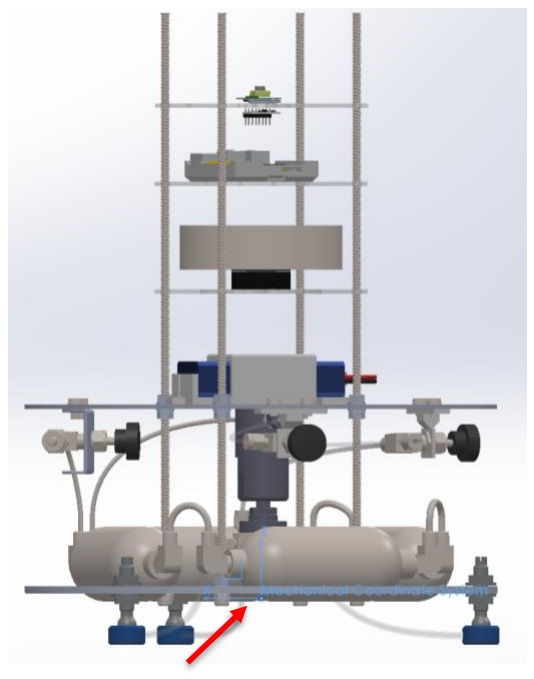
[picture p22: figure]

- 52 -

Order: -

Comments:

Formula:

Diagram:

Figure 8-6. CAD Reference Frame. The point is at O (0,0,0) of the CAD Frame.

### 2.2.3 Reaction Wheel Frame

Table 8-6: IMU Reference definition

Type | Title | Mnemonic | ID
Rotating Reference Frame | Reaction Wheel Frame | RWF | M-B-01

Definition:

+X_CAM | The X points to one of the sides of the Wheel.
+Y_CAM | The Y axis completes the Triad.
+Z_CAM | The Z axis is parallel to the Z axis (+Z_CAD) of the mechanical reference frame
Origin | Reaction Wheel System Centre of Mass.

Rationale: The Reaction wheel system is not at the centre of the robot.

Transformation: From Mechanical CAD to RWF.

Translation: Translation along the Z axis of the CAD reference frame.

- 53 -

[WMT

] = [0 0 0.2373]

Tmeters

Rotation:

Rotation about the Z axis as the Reaction Wheel is a non-inertial frame. [WM]R = [

cos ψ sin ψ 0
− sin ψ cos ψ 0
0 | 0 | 1

]

Order: -[WM] = R3
(ψ)

Comments:

Formula:
[

X
Y
Z

]

RWF

= [

1 0 | 0
0 1 | 0
0 0 14

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
0.2373

]

Diagram:

Figure 8-7. Reaction Wheel Frame vs Mechanical CAD Frame.

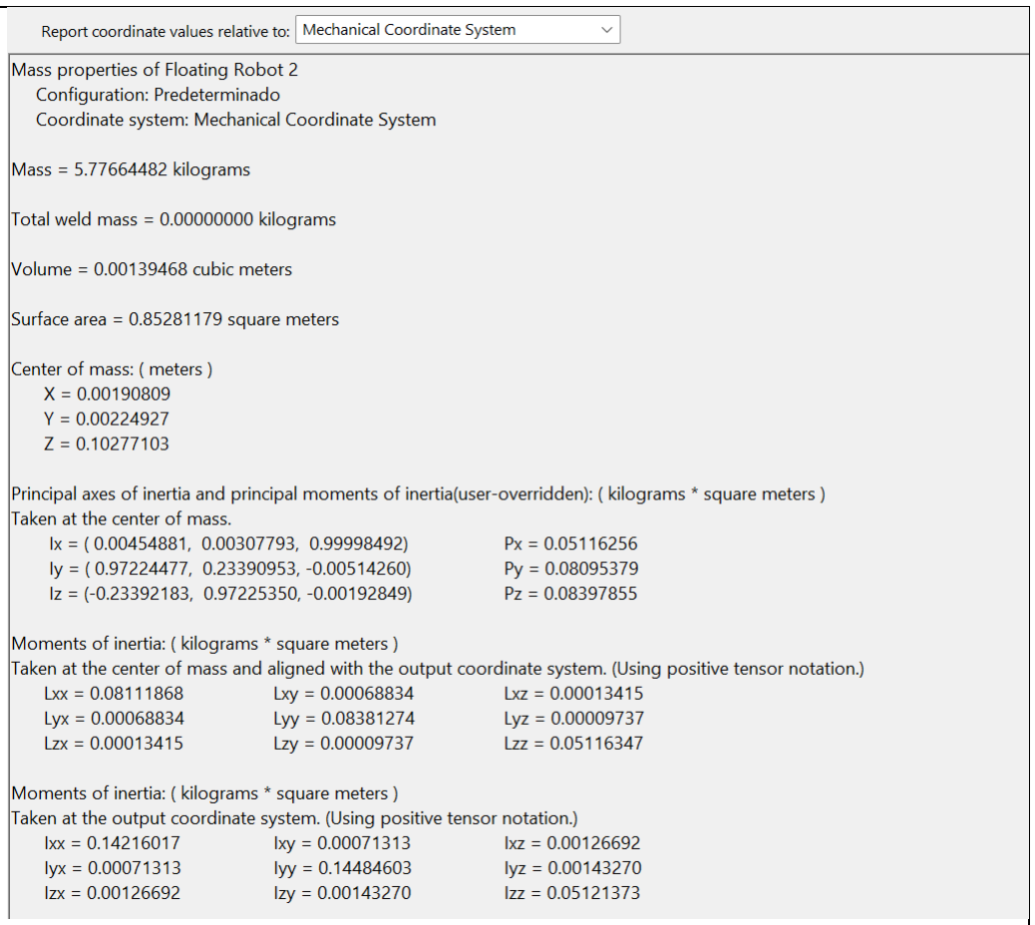
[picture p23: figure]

- 54 -

### 2.2.4 Camera Reference Frame

Table 8-7: CAM Reference Frame

Type | Title | Mnemonic | ID
Fixed Reference Frame | Camera Reference Frame | CAM | M-B-02

Definition:

+X_CAM | The X axis completes the triad.
+Y_CAM | The Y axis points downwards the camera.
+Z_CAM | The Z axis points outside the camera.
Origin | Image sensor of the camera

Rationale: The image sensor of the camera is not at the centre of the mount. Real position is

obtained from the CAD file.

Transformation: From Mechanical CAD to CAM.

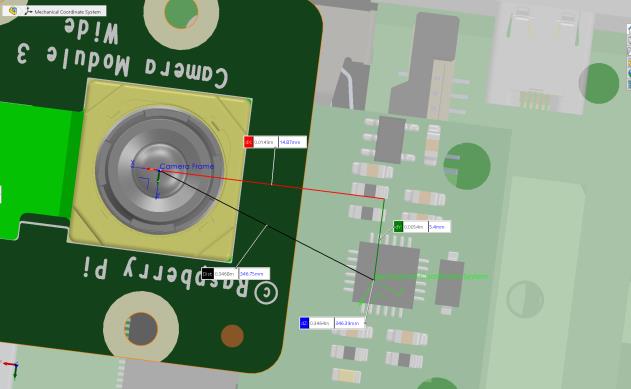
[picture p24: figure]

- 55 -

Translation: Translation along the three axes of the CAD reference frame. [CMT

] = [0.0180 0.2436 0.0011]

Tmeters

Rotation: Fixed rotation about the Z axis:φ = 67.23 deg, θ = 67.23 deg, ψ = 0 [CM] = [

0.3870 0.9221 0
−0.9221 0.3870 0
0 | 0 | 1

]

Order:

Comments: The size of the translation depends on the model of camera and where the image

sensor is positioned with respect to the base of the camera.

Formula:
[

X
Y
Z

]

CAM

= [

0.3870 0.9221 0
−0.9221 0.3870 0
0 | 0 | 1

][

x
y
z

]

CAD

Rotation
+ [

0.01487
−0.0054
0.3464

]

CAD

Translation

Diagram:

- 56 -

Figure 8-8. Camera Reference Frame (CAM), Mechanical Frame (CAD).

### 2.2.5 Inertial Sensor Frame

Table 8-8: IMU Reference definition

Type | Title | Mnemonic | ID
Rotating Reference Frame | Inertial Sensor Reference Frame | IMU | M-B-02

Definition:

+X_CAM | The X axis is parallel to the X axis (+X_CAD) of the mechanical reference frame
+Y_CAM | The Y axis is parallel to the Y axis (Y+_CAD) of the mechanical reference frame
+Z_CAM | The Z axis is parallel to the Z axis (+Z_CAD) of the mechanical reference frame
Origin | Gyroscope Sensor Centre of Mass.

Rationale: The gyroscope sensor is not at the centre of the robot.

Transformation: From Mechanical CAD to IMU (from Mechanical)

Translation: Translation along the three axes of the CAD reference frame:

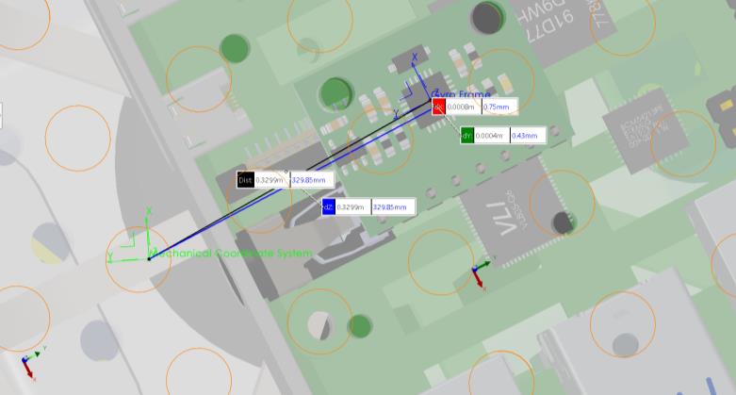
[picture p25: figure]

- 57 -

[GM]T = [0.0006 0.0031 0.2271]

T meters

Rotation: Fixed rotation about φ = 22.77 deg, θ = 22.77 deg, ψ = 0 deg. [GM]R = [

0.9225 | −0.3859 0
−0.3859 | 0.9225 | 0
0 | 0 | 1

]

Order: [GC] = R3
(φ)

Comments:

Formula:
[

X
Y
Z

]

IMU

= [

0.9225 | −0.3859 0
−0.3859 | 0.9225 | 0
0 | 0 | 1

][

x
y
z

]

CAD

+ [

0.0008
0.0004
0.3299

] m

Diagram:

Figure 8-9. Distance from Mechanical Frame to Gyro Frame

Figure 8-10. Gyroscope Frame and Mechanical CAD Frame.

- 58 -

APPENDIX B: MATLAB Scripts & Simulink Models

All MATLAB Scripts, Simulink Models, Images and code files were submitted to the next GitHub

Repository:

https://github.com/JorgeACM/Reaction-Wheel-Control.git.

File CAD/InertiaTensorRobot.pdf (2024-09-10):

Mass properties of Floating Robot 2 Configuration: Predeterminado
Coordinate system: Main Coordinate System

Mass = 5.77664482 kilograms

Total weld mass = 0.00000000 kilograms

Volume = 0.00139468 cubic meters

Surface area = 852811.79038465 square millimeters

Center of mass: ( millimeters )
X = 0.00000000
Y = 0.00000000
Z = 0.00000000

Principal axes of inertia and principal moments of inertia(user-overridden): ( kilograms * square millimeters ) Taken at the center of mass.
Ix = ( 0.99991423, 0.01201015, 0.00522297) | Px = 51162.56407942
Iy = (-0.01201211, 0.99992779, 0.00034410) | Py = 80953.78607720
Iz = (-0.00521846, -0.00040681, 0.99998630) | Pz = 83978.54593565

Moments of inertia: ( kilograms * square millimeters )
Taken at the center of mass and aligned with the output coordinate system. (Using positive tensor notation.)
Lxx = 51167.75633783 | Lxy = 357.76003588 Lxz = 171.36982793
Lyx = 357.76003588 Lyy = 80949.48937923 | Lyz = 3.09924817
Lzx = 171.36982793 Lzy = 3.09924817 | Lzz = 83977.65037522

Moments of inertia: ( kilograms * square millimeters )
Taken at the output coordinate system. (Using positive tensor notation.)
Ixx = 51167.75633783 | Ixy = 357.76003588 Ixz = 171.36982793
Iyx = 357.76003588 Iyy = 80949.48937923 | Iyz = 3.09924817
Izx = 171.36982793 Izy = 3.09924817 | Izz = 83977.65037522

Mass Properties have been overridden at the assembly level. Therefore, any overrides specified at the component level are ignored in
Moment of Inertia calculations. One or more components have user-overridden mass properties that are being ignored: kcp1fra2a2p10000-swagelokcompany-3d-03-27-2024_BOTTOM<Predeterminado>@Pressure_valve<1><Predeterm LiPo-Battery<1><Varsayılan>@Battery-with-case<1><Predeterminado>
GM3506 With Encoder@AOCS-2
PCB, RPi4ModelB<1><Default>@Raspberry Pi 4 Model B<1><Default>@RaspberryPi-Case<1><Default>@Electro 2.54 mm DUPONT MALE PIN HEADER, IO, 2X20, RPi4ModelB<1><Default>@Raspberry Pi 4 Model B<1><Default Gigabit Ethernet Port, RPi4ModelB<1><Default>@Raspberry Pi 4 Model B<1><Default>@RaspberryPi-Case<1><D Female Micro HDMI Connector, RPi4ModelB<2><Default>@Raspberry Pi 4 Model B<1><Default>@RaspberryPi-Ca Female Micro HDMI Connector, RPi4ModelB<3><Default>@Raspberry Pi 4 Model B<1><Default>@RaspberryPi-Ca Female USB Type C Connector, RPi4ModelB<1><Default>@Raspberry Pi 4 Model B<1><Default>@RaspberryPi-Ca 2X USB3.0 PORTS, RPi4ModelB<2><Default>@Raspberry Pi 4 Model B<1><Default>@RaspberryPi-Case<1><Def SD Card Slot, RPi4ModelB<1><Default>@Raspberry Pi 4 Model B<1><Default>@RaspberryPi-Case<1><Default>@ 2X USB2.0 PORTS, RPi4ModelB<1><Default>@Raspberry Pi 4 Model B<1><Default>@RaspberryPi-Case<1><Def Camera_module_3_wide_model_simple.stp@Camera-Gyro-Assembly

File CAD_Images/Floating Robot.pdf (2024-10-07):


Producto SOLIDWORKS Educational. Solo para uso en la enseñanza.

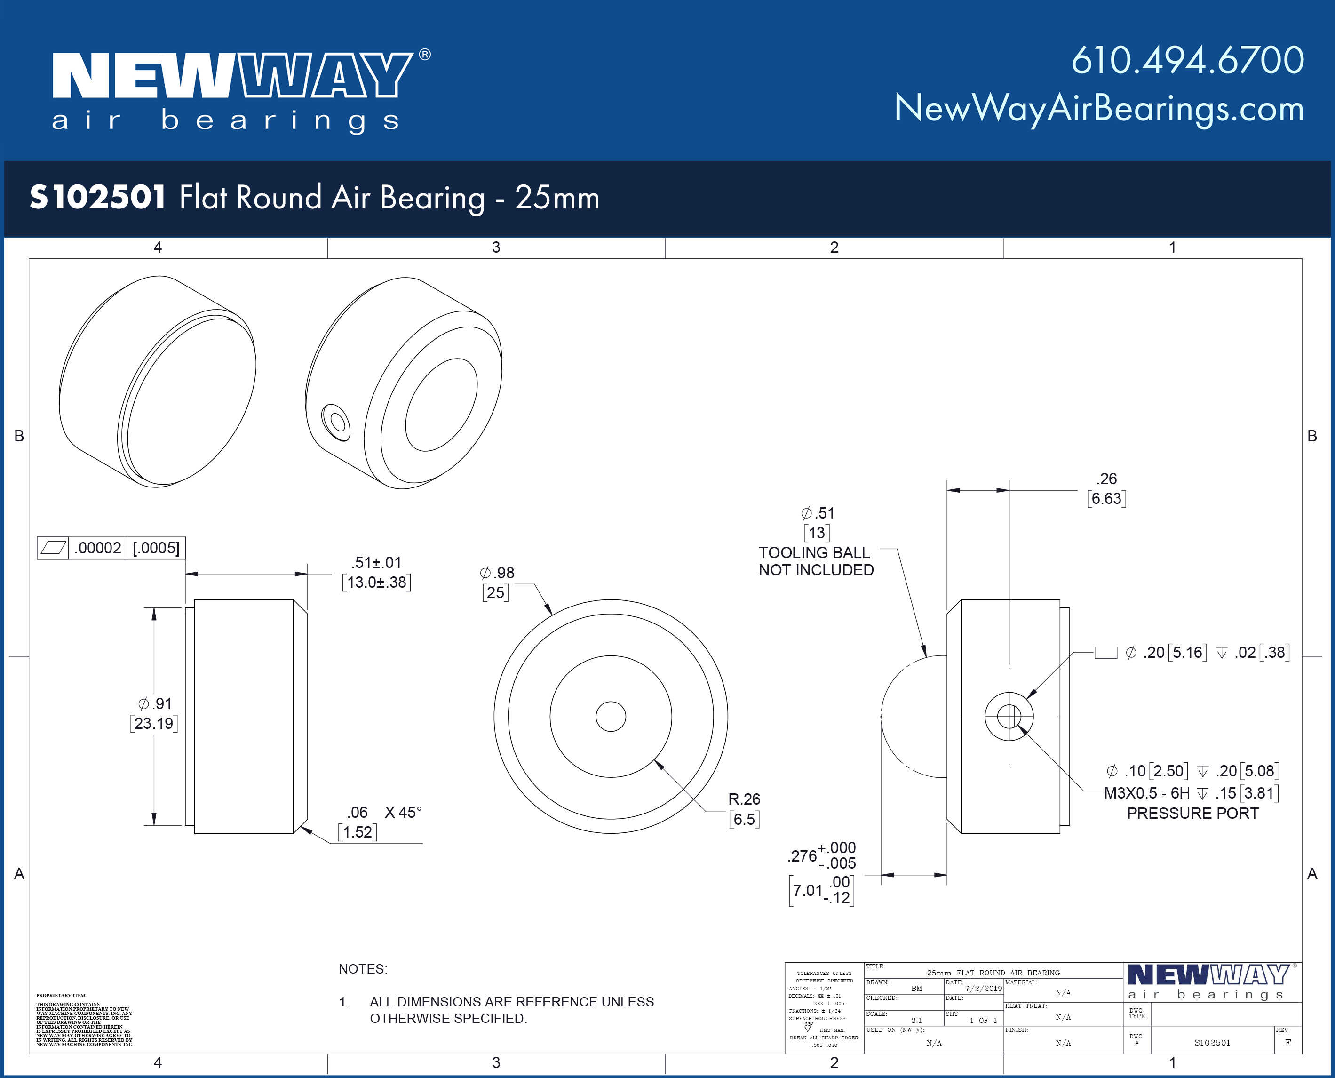
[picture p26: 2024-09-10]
CAD/Schematics/S102501-1.jpg

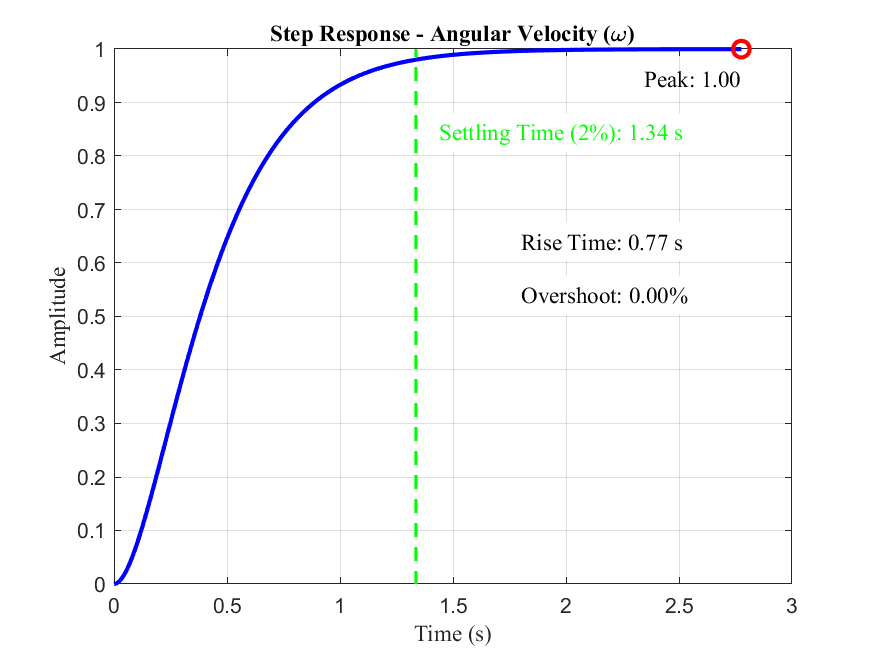
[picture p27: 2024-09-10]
Images/omega_response.png

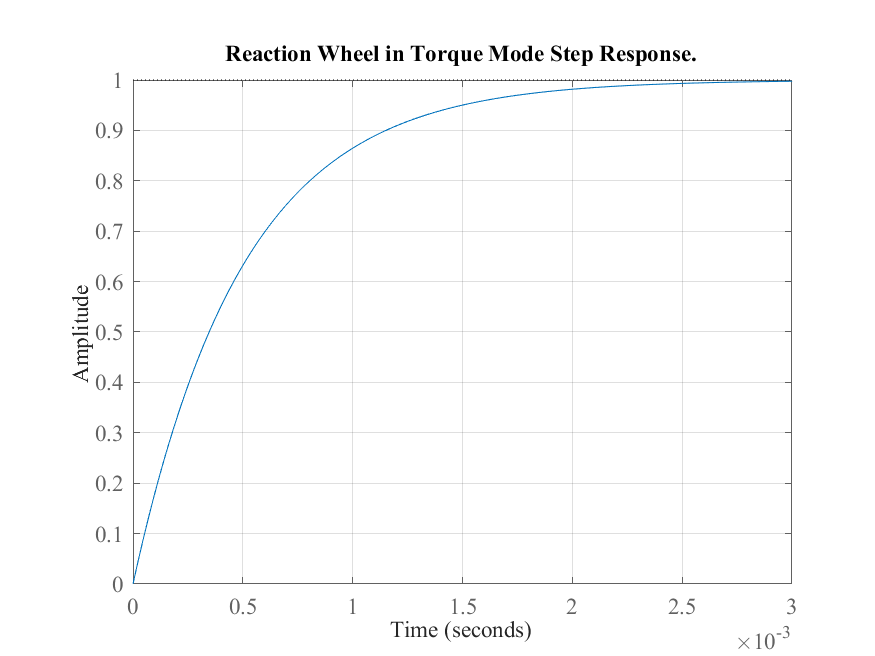
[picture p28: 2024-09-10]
Images/SimplifiedTorqueModeRW.png

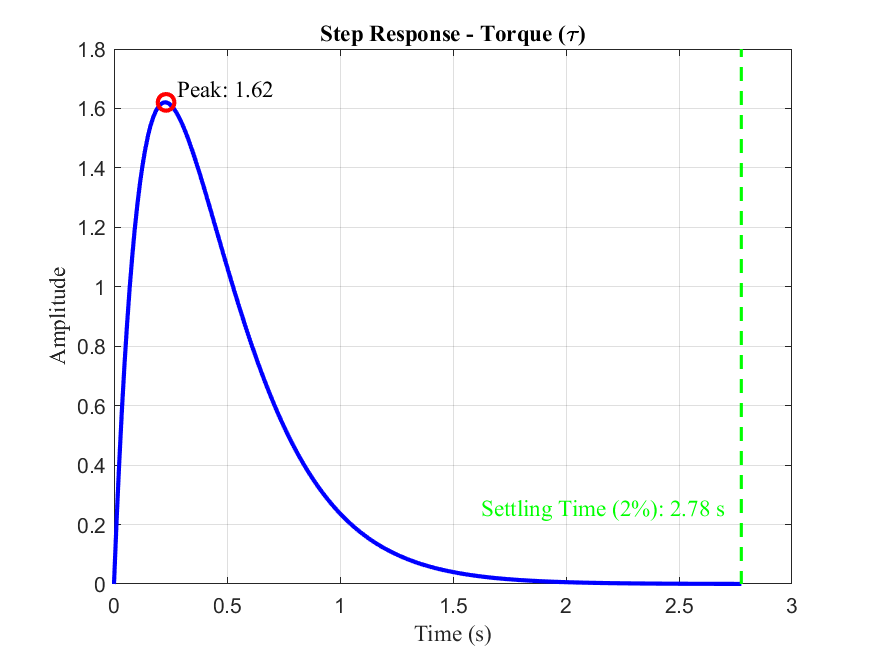
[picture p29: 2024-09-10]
Images/tau_response.png

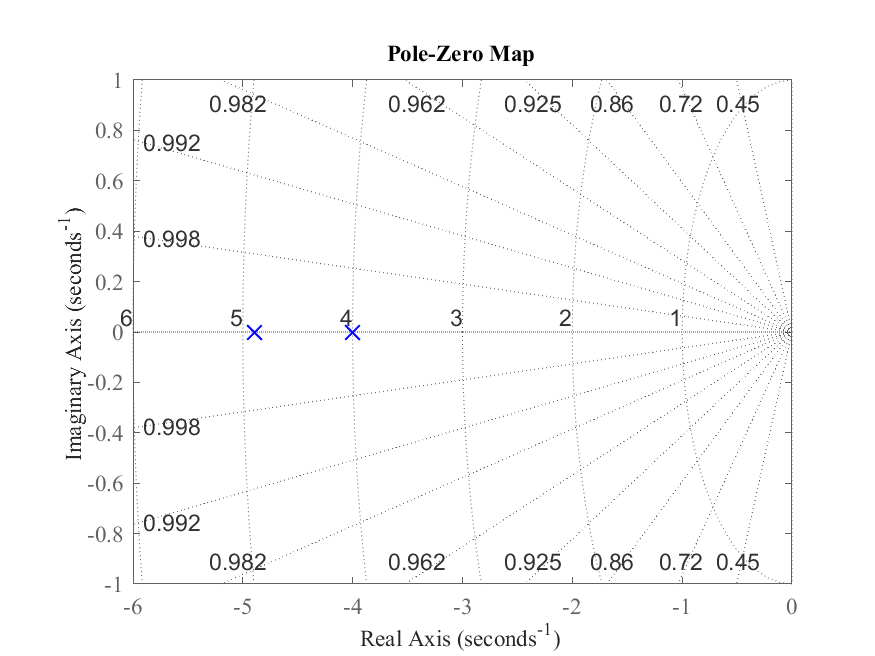
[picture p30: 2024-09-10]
Images/PoleZeroMap_OuterLoop.png

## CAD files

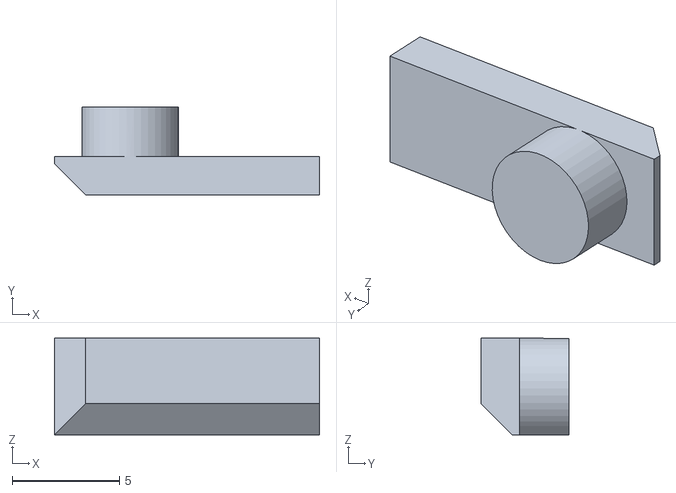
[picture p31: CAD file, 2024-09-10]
CAD/raspberry-pi/RaspberryCaseSTL/final_assembly - Copy - Rubber pads - Copy-1.STL
12.3 x 4.10 x 4.50

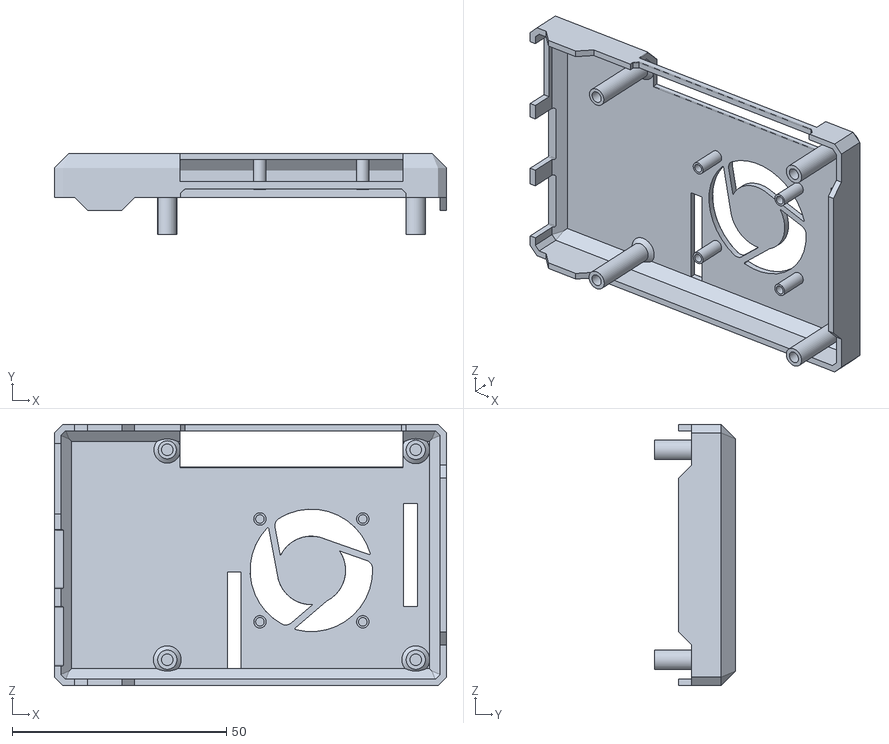
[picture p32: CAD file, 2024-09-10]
CAD/raspberry-pi/RaspberryCaseSTL/final_assembly - Copy - TOP-1.STL
91.5 x 19.0 x 61.0

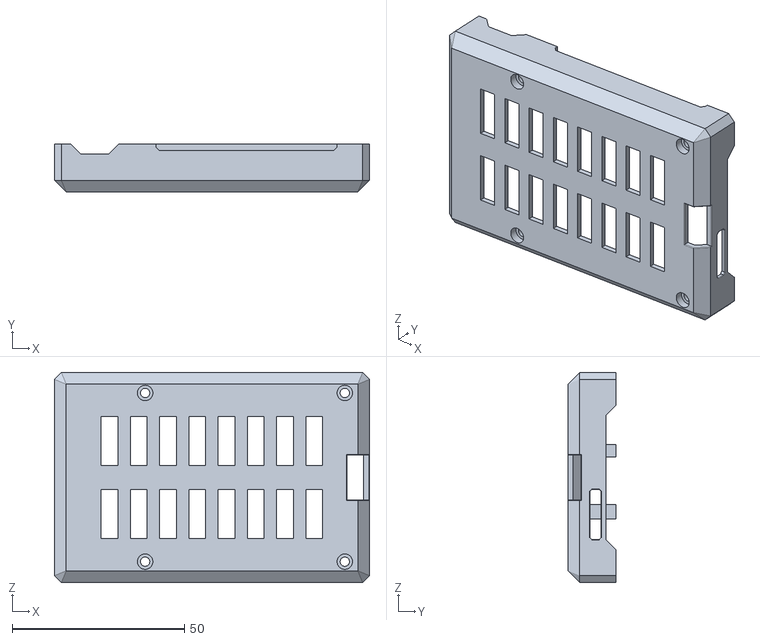
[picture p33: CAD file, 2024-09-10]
CAD/raspberry-pi/RaspberryCaseSTL/final_assembly - Copy - base-2.STL
91.5 x 14.0 x 61.0

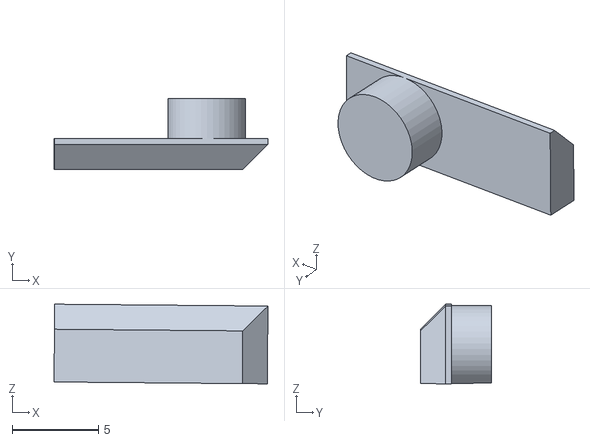
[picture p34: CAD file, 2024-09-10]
CAD/raspberry-pi/RaspberryCaseSTL/final_assembly - Copy - Rubber pads - Copy-2.STL
12.4 x 4.10 x 4.61

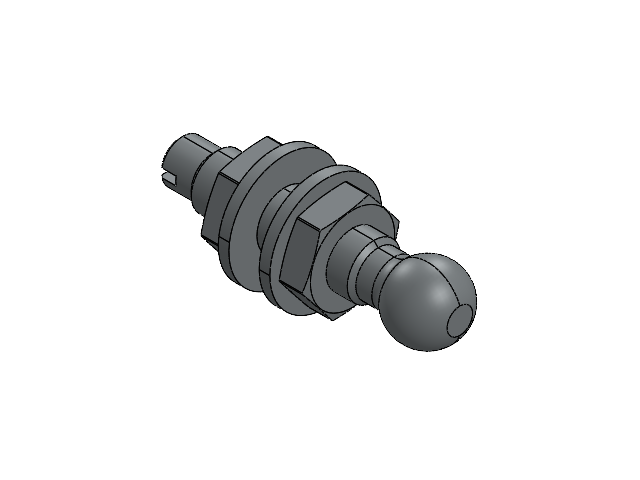
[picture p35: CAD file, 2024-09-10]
CAD/Bearing/S8013B06_2.SLDASM
S8013B05_S8013B05.step
S80XXNXX_S8010N03.step x 2
S92FS01.step x 2

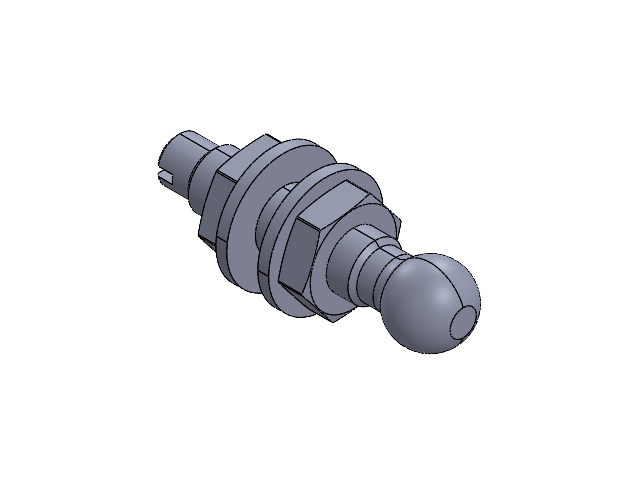
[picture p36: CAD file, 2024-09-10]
CAD/iflight-ipower-gbm3506-130t-with-encoder-1.snapshot.8/S8013B06-3.SLDASM
S8013B05_S8013B05.step
S80XXNXX_S8010N03.step x 2
S92FS01.step x 2

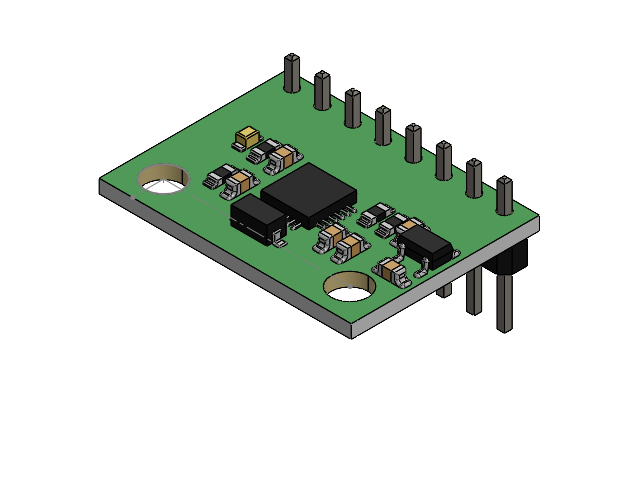
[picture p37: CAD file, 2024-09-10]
CAD/mpu-6050-imu-sensor-1.snapshot.5/MPU 6050 IMU2.SLDASM
Base_1.STEP
pin header_1.STEP x 8
sensor chip.STEP
S2NH chip_1.STEP
Resistor small_1.STEP x 6
Resistor small black_1.STEP x 4
Small LED_1.STEP
Resistor black_1.STEP

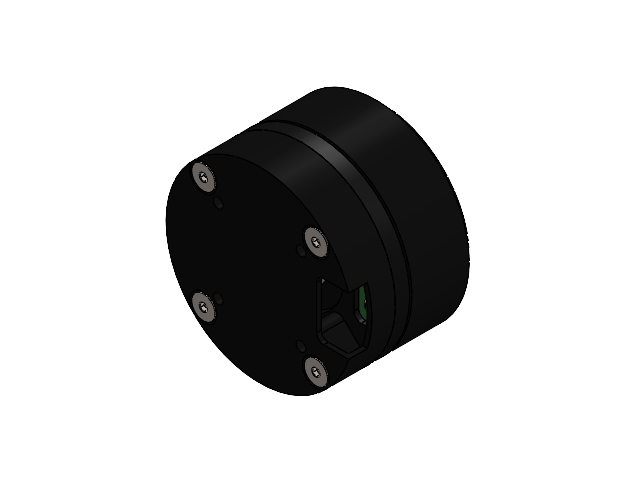
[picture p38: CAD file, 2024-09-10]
CAD/GM3506 With Encoder motor v2.SLDASM
По умолчанию.step
Rotor-0.step
Rotor-1.step
Rotor-2.step
По умолчанию (1).step
Stator-3.step
Stator-4.step
Magnet.step
Encoder.step
93395A179_316 Stainless Steel Hex Drive Flat Head Screw.step x 4

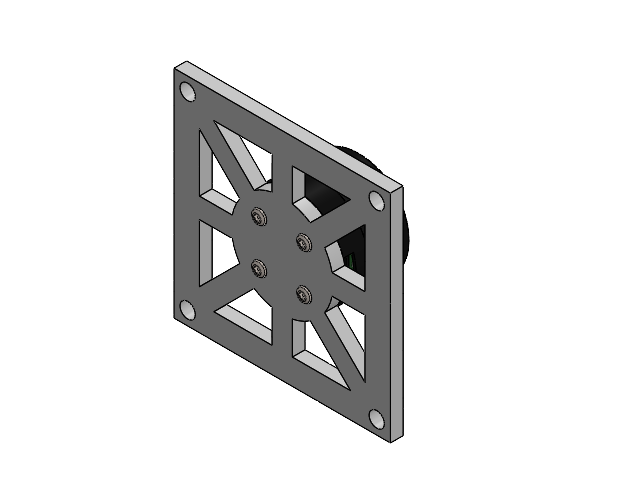
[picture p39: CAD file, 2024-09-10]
CAD/iflight-ipower-gbm3506-130t-with-encoder-1.snapshot.8/MotorAndBase.SLDASM
По умолчанию_2.step
Rotor-0_1.step
Rotor-1_1.step
Rotor-2_1.step
По умолчанию_1.step
Stator-3_1.step
Stator-4_1.step
Magnet.step
Encoder_1.step
93395A179_316 Stainless Steel Hex Drive Flat Head Screw_1.step x 4
Motor Base
hexalobular socket pan head_iso x 4

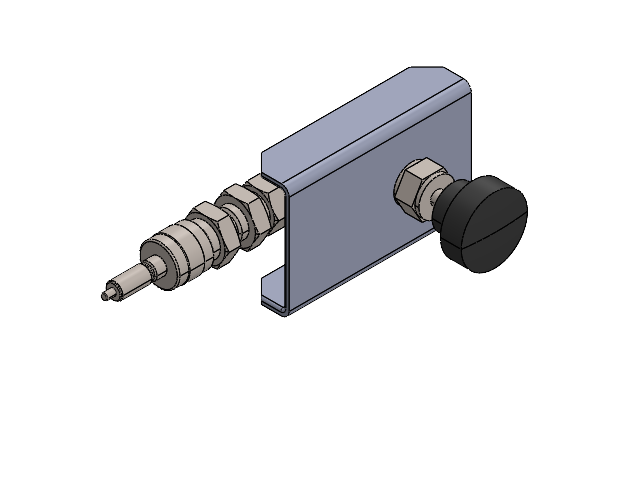
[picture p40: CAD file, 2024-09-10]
CAD/air-connection.SLDASM
adapter
Quick connector.stp
tube connector1
ss-oks2-swagelokcompany-3d-03-27-2024_top
ss-oks2-swagelokcompany-3d-03-27-2024_valve

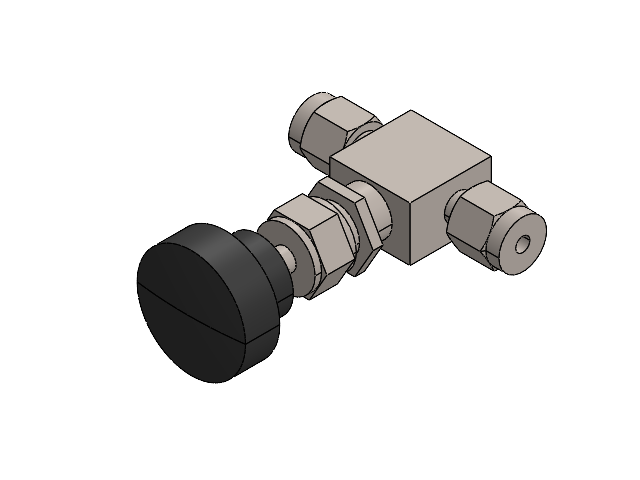
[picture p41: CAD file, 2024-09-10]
CAD/ss-oks2-swagelokcompany.SLDASM
ss-oks2-swagelokcompany-3d-03-27-2024_top
ss-oks2-swagelokcompany-3d-03-27-2024_valve

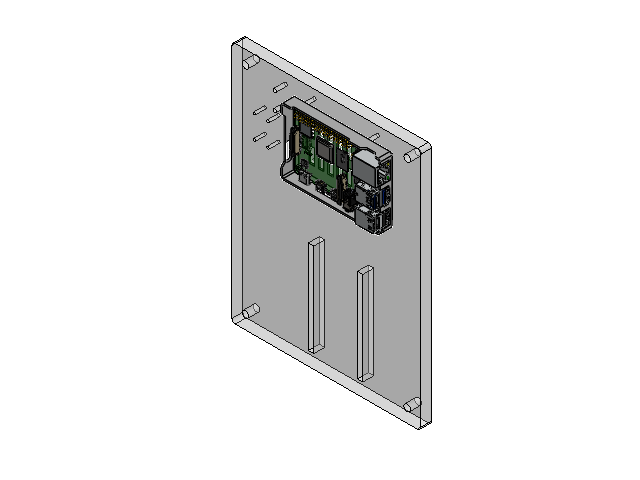
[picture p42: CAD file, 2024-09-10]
CAD/mount+raspberry.SLDASM
raspberry mount
base
PCB, RPi4ModelB
Broadcom BCM2711B0 CPU, RPi4ModelB
2.54 mm DUPONT MALE PIN HEADER, POE, 2X2, RPi4ModelB
2.54 mm DUPONT MALE PIN HEADER, IO, 2X20, RPi4ModelB
Camera Connector, RPi4ModelB
Microphone Plug, RPi4ModelB
Display Connector, RPi4ModelB
Gigabit Ethernet Port, RPi4ModelB
Female Micro HDMI Connector, RPi4ModelB x 2
Female USB Type C Connector, RPi4ModelB
2X USB3.0 PORTS, RPi4ModelB
91D77 D9WHV 778K, 4 GB LPDDR4 SDRAM, RPi4ModelB
Cypress CYW43455 Wireless Module Cover, RPi4ModelB
SD Card Slot, RPi4ModelB
VIA VL805 PCIe USB 3.0 controller, RPi4ModelB
2X USB2.0 PORTS, RPi4ModelB
Broadcom BCM54213PE Gigabit Ethernet Transceiver, RPi4ModelB
MxL7704 Universal PMIC, RPi4ModelB

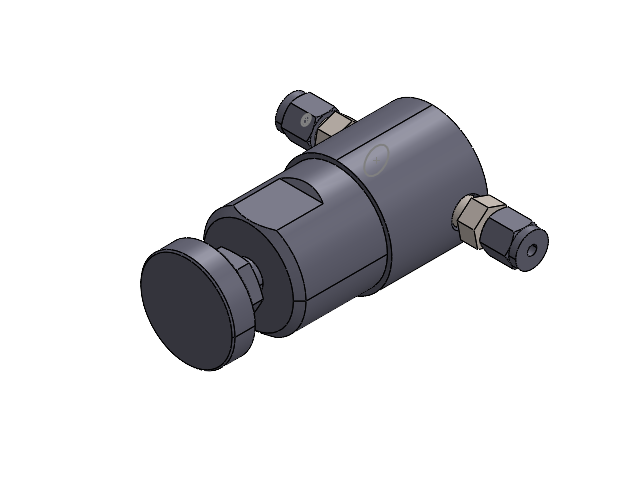
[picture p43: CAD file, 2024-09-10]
CAD/Pressure_valve.SLDASM
kcp1fra2a2p10000-swagelokcompany-3d-03-27-2024_BOTTOM
kcp1fra2a2p10000-swagelokcompany-3d-03-27-2024_TOP
14-to18-male-reductor x 2
ss-202-1-swagelokcompany-3d-04-06-2024.stp x 2

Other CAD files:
CAD/Battery-with-case.SLDASM
CAD/raspberry-pi/RaspberryCaseSTL/final_assembly - Copy - Rubber pads-1.STL
CAD/raspberry-pi/RaspberryCaseSTL/final_assembly - Copy - Rubber pads-5.STL
CAD/14-to18-male-reductor.SLDPRT
CAD/316L-HDF4-150-SwagelokCompany-3D-08-02-2023.SLDPRT
CAD/8mp-raspberry-pi-cam-m12-lens-1.snapshot.2/raspberry_pi_cam_8mp_m12_lens.f3d
CAD/8mp-raspberry-pi-cam-m12-lens-1.snapshot.2/raspberry_pi_cam_8mp_m12_lens.step
CAD/AOCS-2.SLDASM
CAD/AOCS.SLDASM
CAD/Air-bearing.SLDASM
CAD/Battery-Mount-Top.SLDPRT
CAD/Battery-Mount.SLDPRT
CAD/Bearing/S102501.step
CAD/Bearing/S8013B06.SLDASM
CAD/Bearing/S8013B06.step
CAD/Bearing/s102501.SLDPRT
CAD/Bearing/s102501_2.SLDPRT
CAD/Dibujo1.SLDDRW
CAD/Electronic-base-camera.SLDPRT
CAD/Electronic-base.SLDPRT
CAD/Ensamblaje6.SLDASM
CAD/GM3506 With Encoder motor v1.step
CAD/KCP1FRA2A2P10000-SwagelokCompany-3D-03-27-2024.stp
CAD/LiPo-Battery.SLDPRT
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

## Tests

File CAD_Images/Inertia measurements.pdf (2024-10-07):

Propiedades de masa de Floating Robot Configuración: Predeterminado
Sistema de coordenadas: -- predeterminado --

Masa = 4336.97 gramos

Volumen = 948959.52 milímetros cúbicos

Área de superficie = 609276.82 milímetros cuadrados

Centro de masa: ( milímetros )
X = 3.59
Y = 51.43
Z = 2.70

Ejes principales de inercia y momentos principales de inercia: ( gramos * milímetros cuadrados ) Medido desde el centro de masa.
Ix = ( 0.33, 0.10, 0.94) | Px = 42325076.10
Iy = ( 0.93, 0.11, -0.34) | Py = 45398992.48
Iz = (-0.14, 0.99, -0.06) | Pz = 51099562.71

Momentos de inercia: ( gramos * milímetros cuadrados )
Obtenidos en el centro de masa y alineados con el sistema de coordenadas de resultados. (Usando notación tensorial positiva
Lxx = 45171939.71 Lxy = 892876.00 | Lxz = 913139.06
Lyx = 892876.00 | Lyy = 50938785.53 Lyz = 603092.67
Lzx = 913139.06 | Lzy = 603092.67 | Lzz = 42712906.05

Momentos de inercia: ( gramos * milímetros cuadrados)
Medido desde el sistema de coordenadas de salida. (Usando notación tensorial positiva.)
Ixx = 56676340.54 Ixy = 1693533.00 | Ixz = 955101.13
Iyx = 1693533.00 | Iyy = 51026174.16 Iyz = 1204381.54
Izx = 955101.13 | Izy = 1204381.54 | Izz = 54241668.95
